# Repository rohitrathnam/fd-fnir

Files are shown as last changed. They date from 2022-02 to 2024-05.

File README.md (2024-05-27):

# Prototype Instrumentation for Frequency Domain fNIRS

## Abstract

Frequency domain fNIRS is a tissue optical measurement technique used to measure
absolute haemoglobin concentrations in brain tissue. This work is intended to
be the first step in the development of a wearable, low-cost FD-fNIRS device for
neurofeedback applications. The system requirements were generated from a review
of relevant literature. A simplified system architecture was developed based on the
various instrumentation methodologies proposed by various authors. The functional
blocks of this system were prototyped and their performance was evaluated. The
developed VCSEL current source was found to have a span of 10uA which meets the
design specifications. However, challenges exist in optimally biasing SiPM, which is
susceptible to optical and electronic noise sources.

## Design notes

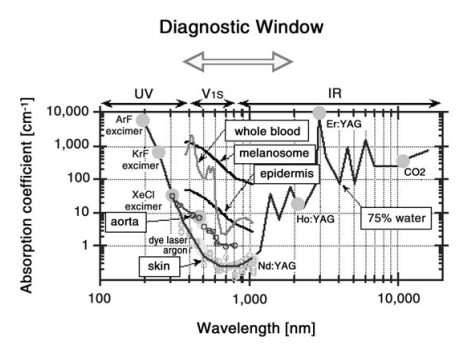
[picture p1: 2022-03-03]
optical_window.png

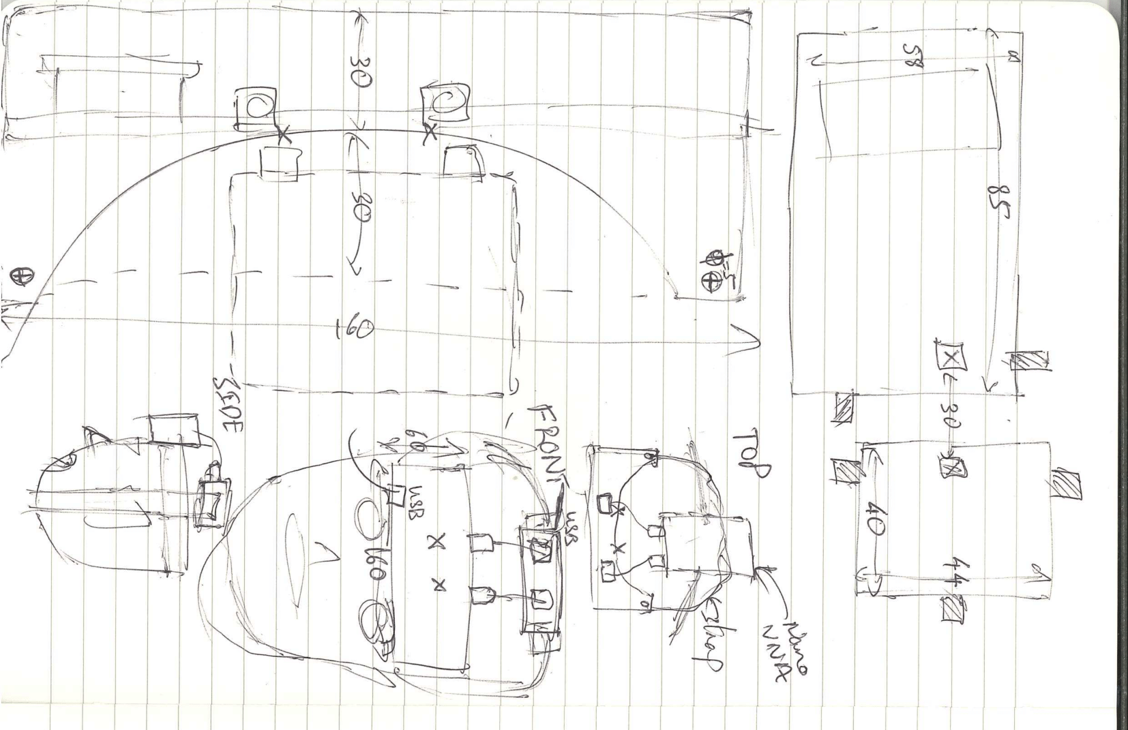
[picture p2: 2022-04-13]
drawings-hand-1.png

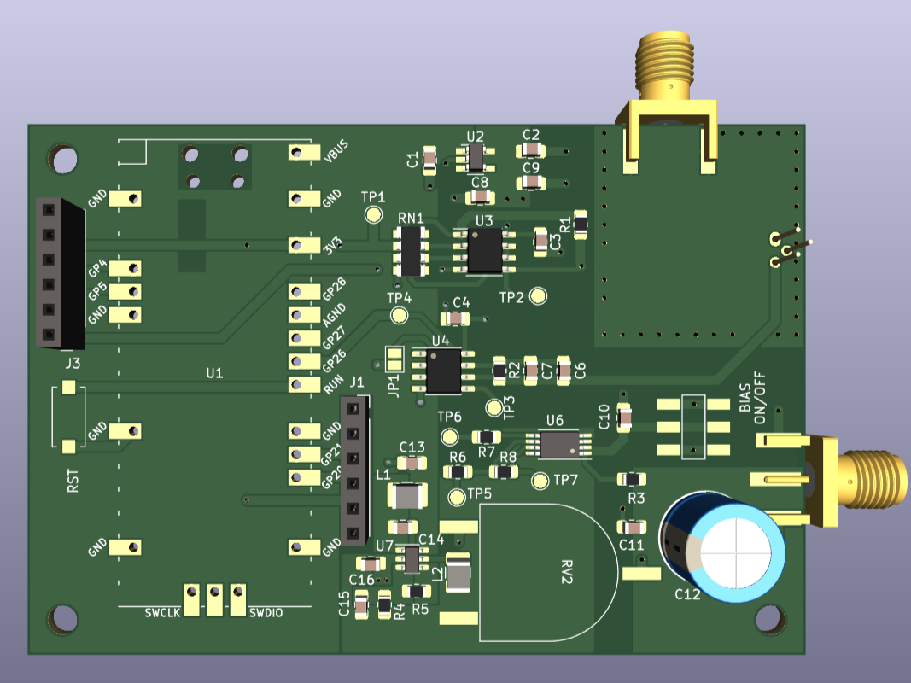
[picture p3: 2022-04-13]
driver-board/driver-board-front.png

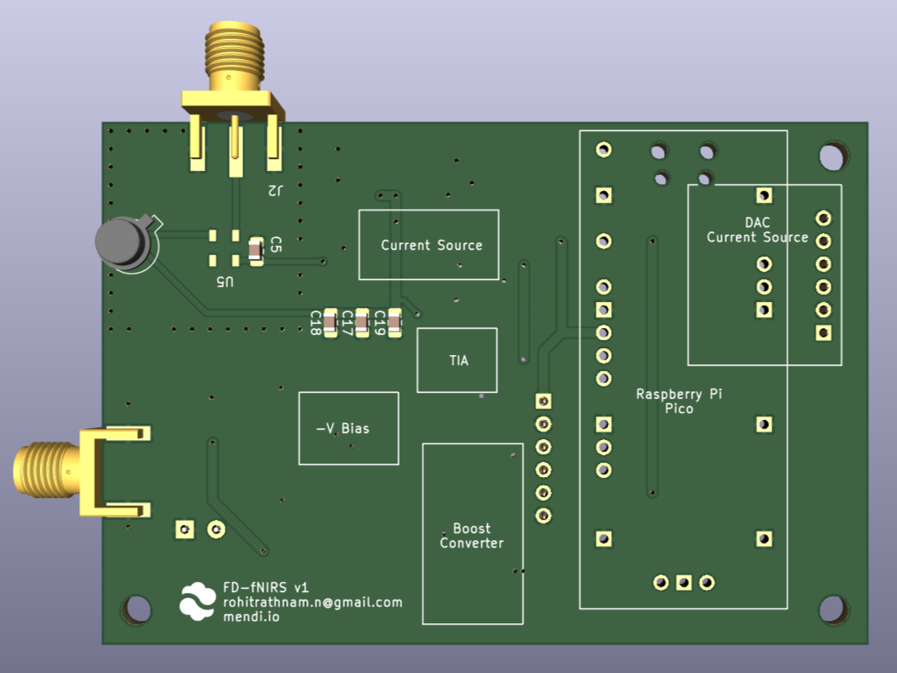
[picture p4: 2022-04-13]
driver-board/driver-board-back.png

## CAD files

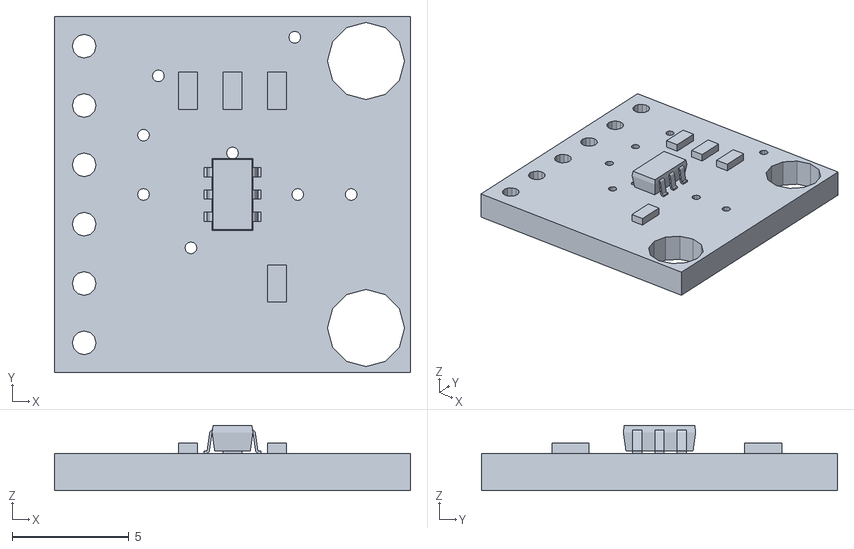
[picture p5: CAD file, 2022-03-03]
driver-board/MCP4725_Breakout.stl
15.2 x 15.2 x 2.80

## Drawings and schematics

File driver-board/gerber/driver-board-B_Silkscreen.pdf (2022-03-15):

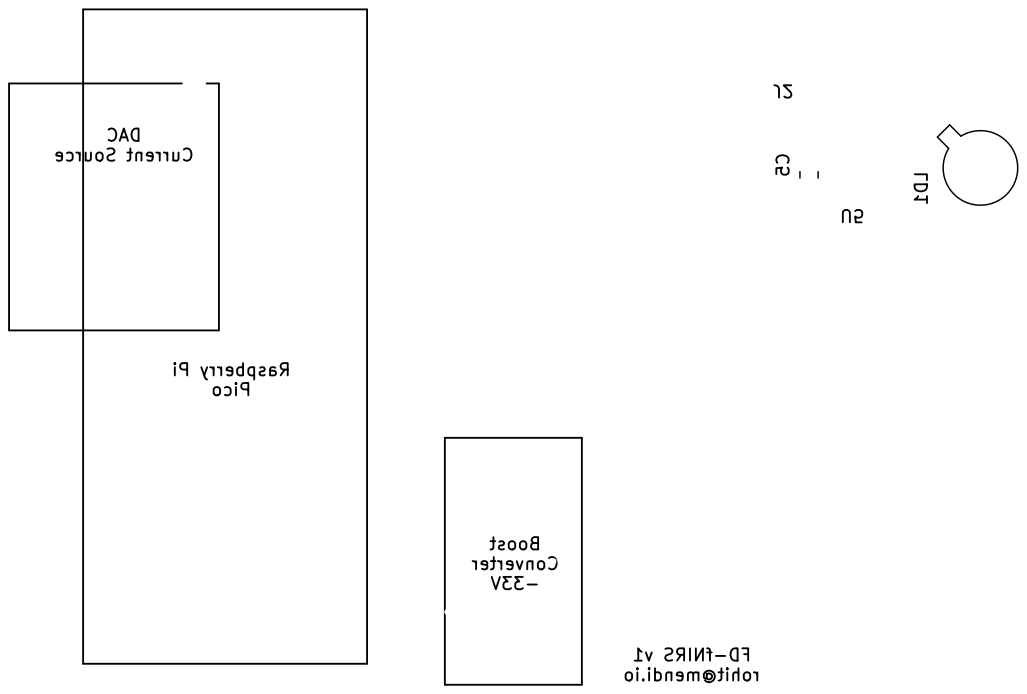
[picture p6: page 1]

Current Source FD-fNIRS v1

rohit@mendi.io Boost Converter

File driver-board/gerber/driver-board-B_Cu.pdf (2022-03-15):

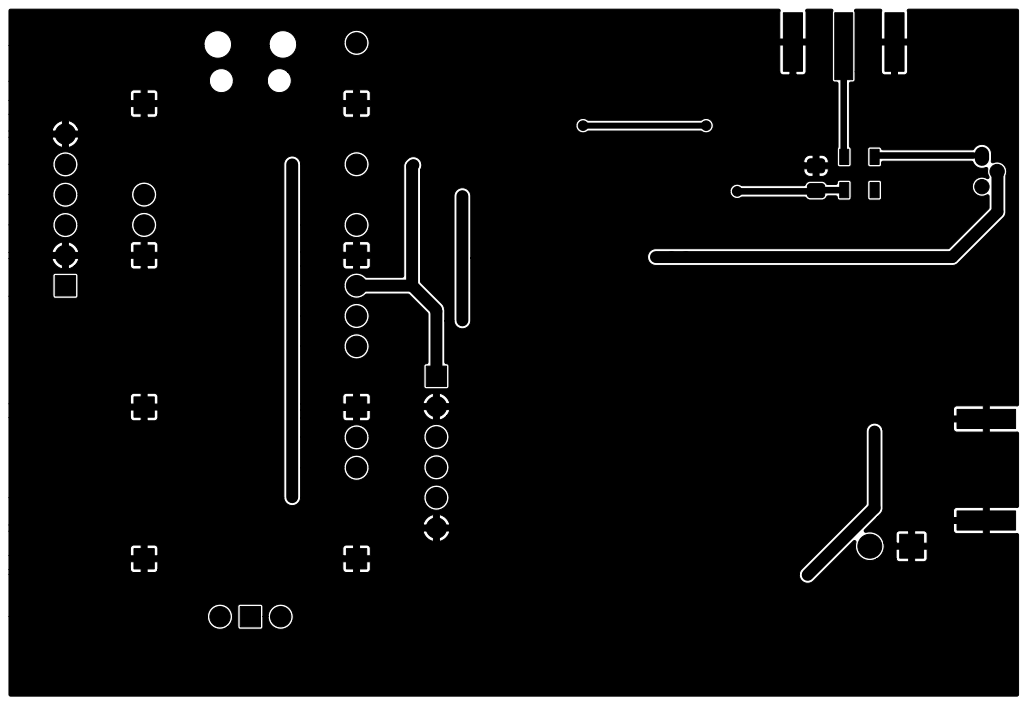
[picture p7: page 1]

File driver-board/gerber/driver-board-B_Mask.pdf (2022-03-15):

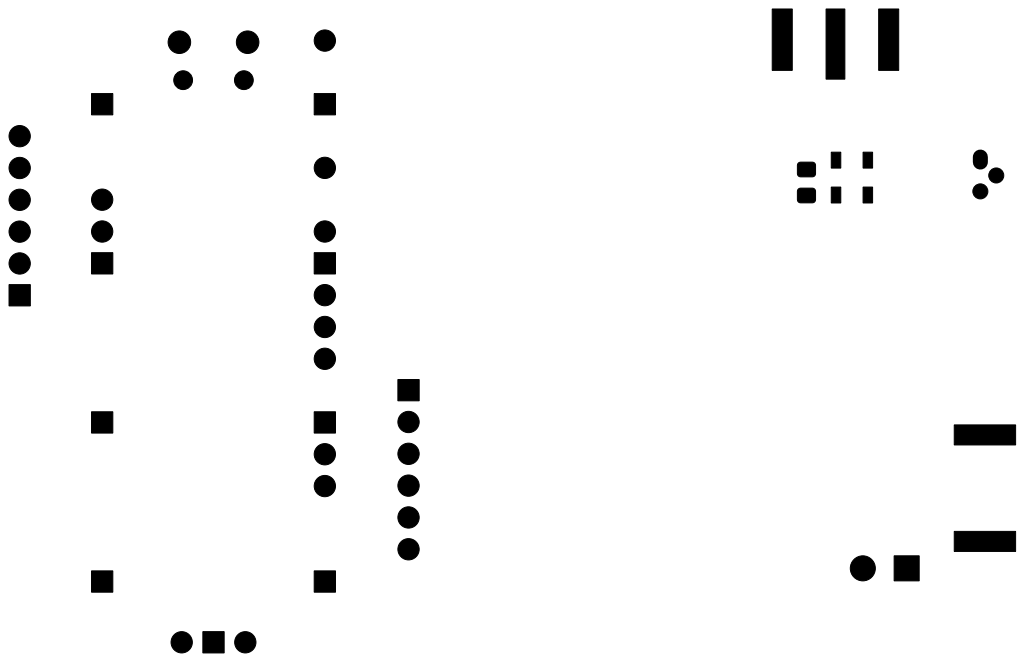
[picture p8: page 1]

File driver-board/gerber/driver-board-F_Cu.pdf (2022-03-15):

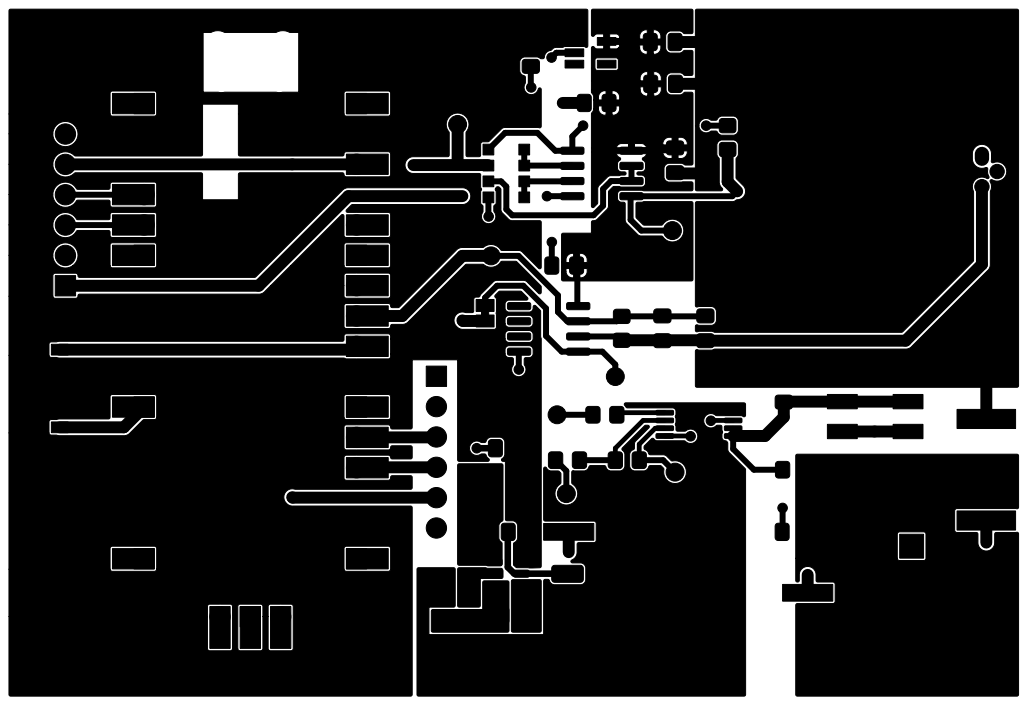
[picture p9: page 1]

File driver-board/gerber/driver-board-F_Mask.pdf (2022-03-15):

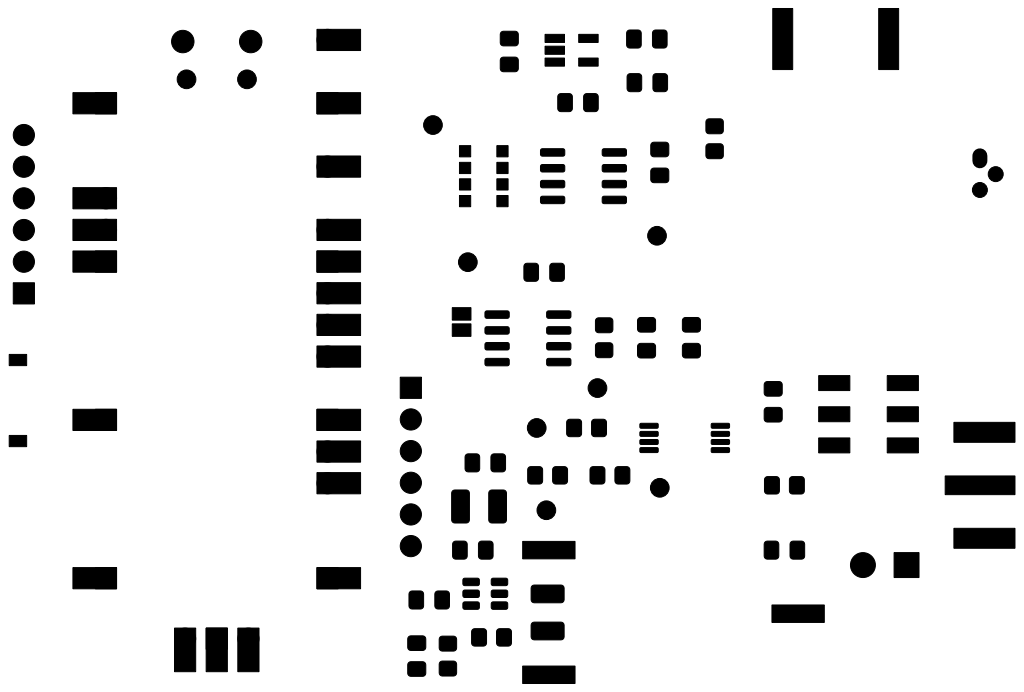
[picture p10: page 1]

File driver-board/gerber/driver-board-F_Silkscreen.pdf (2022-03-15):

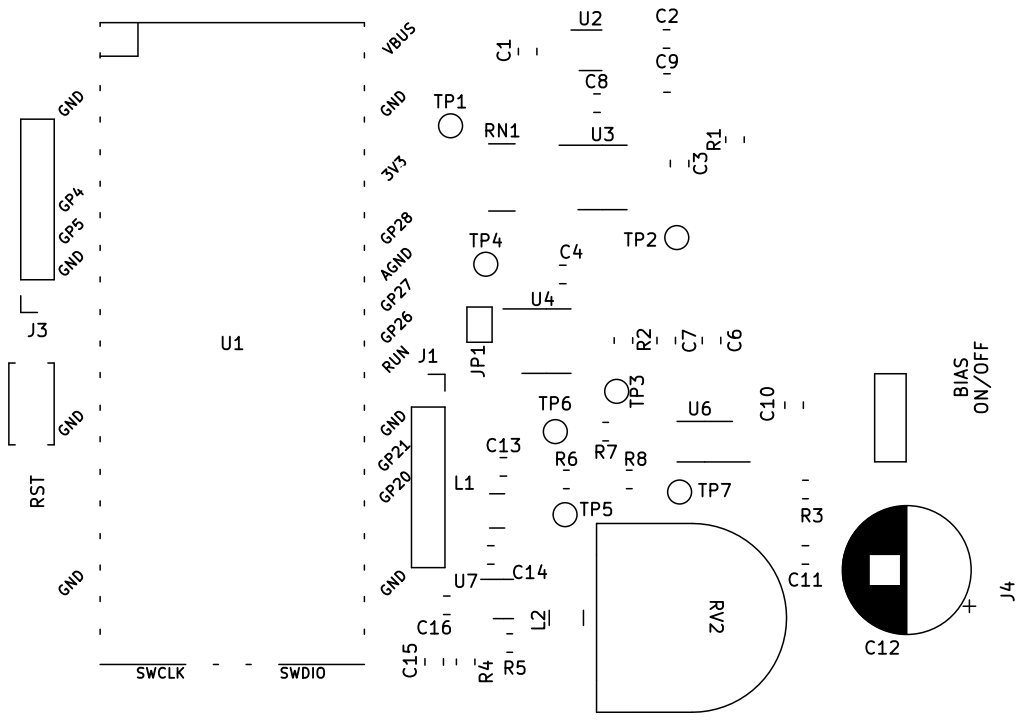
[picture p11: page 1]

RST BIAS ON/OFFU1 RUN GND GND GND GP21 AGND

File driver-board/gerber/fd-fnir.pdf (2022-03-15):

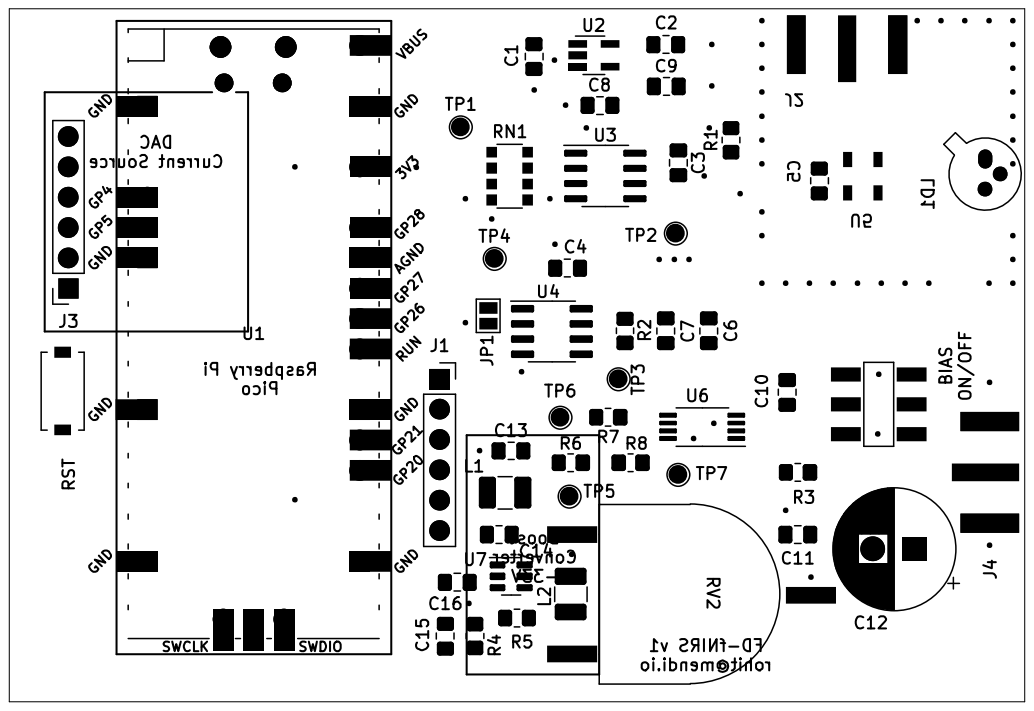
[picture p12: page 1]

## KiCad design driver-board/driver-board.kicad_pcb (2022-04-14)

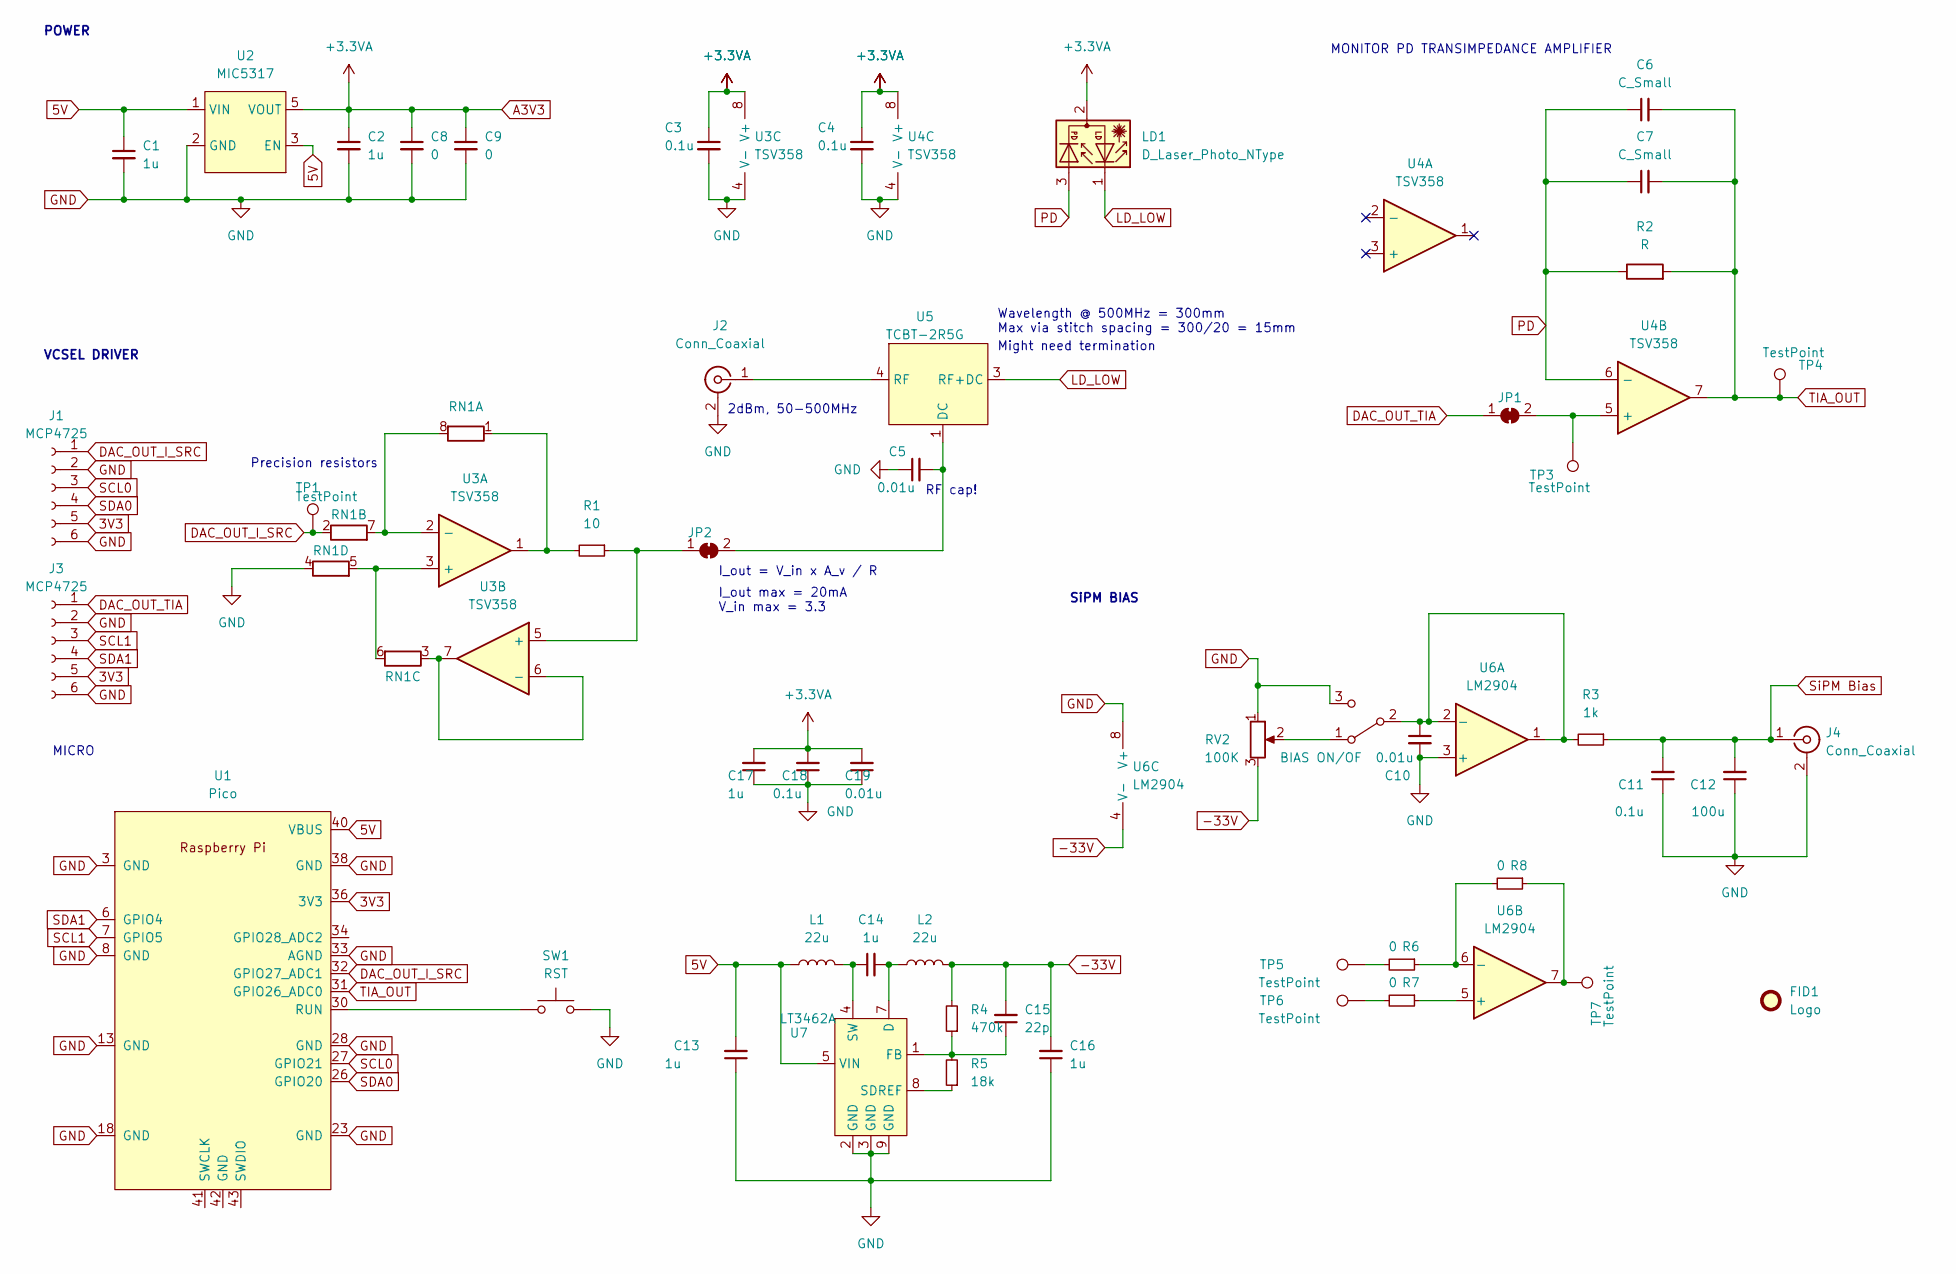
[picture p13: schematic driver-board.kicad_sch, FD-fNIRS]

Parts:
C1, C2, C13, C14, C16, C17: 1u; C_0805_2012Metric_Pad1.18x1.45mm_HandSolder
C3, C4, C11, C18: 0.1u; C_0805_2012Metric_Pad1.18x1.45mm_HandSolder
C5, C10, C19: 0.01u; C_0805_2012Metric_Pad1.18x1.45mm_HandSolder
C6, C7: C_Small; C_0805_2012Metric_Pad1.18x1.45mm_HandSolder
C8, C9: 0; C_0805_2012Metric_Pad1.18x1.45mm_HandSolder
C12: 100u; CP_Radial_D10.0mm_P3.50mm
C15: 22p; C_0805_2012Metric_Pad1.18x1.45mm_HandSolder
FID1: Logo; mendi-logo-plain
J1, J3: MCP4725; PinSocket_1x06_P2.54mm_Vertical
J2, J4: Conn_Coaxial; CONSMA020.062-G
JP1: SolderJumper_2_Open; SolderJumper-2_P1.3mm_Bridged_Pad1.0x1.5mm
JP2: SolderJumper_2_Bridged; SolderJumper-2_P1.3mm_Bridged_Pad1.0x1.5mm
L1, L2: 22u; L_1210_3225Metric_Pad1.42x2.65mm_HandSolder
LD1: D_Laser_Photo_NType; TO-46-3
R1: 10; R_0805_2012Metric_Pad1.20x1.40mm_HandSolder
R2: R; R_0805_2012Metric_Pad1.20x1.40mm_HandSolder
R3: 1k; R_0805_2012Metric_Pad1.20x1.40mm_HandSolder
R4: 470k; R_0805_2012Metric_Pad1.20x1.40mm_HandSolder
R5: 18k; R_0805_2012Metric_Pad1.20x1.40mm_HandSolder
R6, R7, R8: 0; R_0805_2012Metric_Pad1.20x1.40mm_HandSolder
RN1: R_Pack04_SIP_Split; ACASA5002S5002P1AT
RV2: 100K; PT15-RV15
SW1: RST; PTS636 SM43J
SW2: BIAS ON/OF; JS202011SCQN
TP1, TP3, TP4, TP5, TP6, TP7: TestPoint; TestPoint_Pad_D1.5mm
U1: Pico; RPi_Pico_minimal
U2: MIC5317; SOT-23-5_HandSoldering
U3, U4: TSV358; SOIC-8-1EP_3.9x4.9mm_P1.27mm_EP2.29x3mm
U5: TCBT-2R5G; TCBT
U6: LM2904; TSSOP-8_4.4x3mm_P0.65mm
U7: LT3462A

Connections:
3V3: J1.5, J3.5, U1.36 (3V3)
5V: C1.1, C13.2, L1.1, U1.40 (VBUS), U2.1 (VIN), U2.3 (EN), U7.5 (VIN)
-33V: C15.2, C16.2, L2.2, R4.2, RV2.3, U6.4 (V-)
A3V3: C2.1, C3.1, C4.1, C8.1, C9.1, C17.2, C18.2, C19.2, LD1.2, U2.5 (VOUT), U3.8 (V+), U4.8 (V+)
DAC_OUT_I_SRC: J1.1, RN1.2 (R2.1), TP1.1, U1.32 (GPIO27_ADC1)
DAC_OUT_TIA: J3.1, JP1.1 (A)
GND: C1.2, C2.2, C3.2, C4.2, C5.1, C8.2, C9.2, C10.2, C11.1, C12.1, C13.1, C16.1, C17.1, C18.1, C19.1, J1.2, J1.6, J2.2 (Ext), J3.2, J3.6, J4.2 (Ext), RN1.4 (R4.1), RV2.1, SW1.2, SW2.3 (C), U1.3 (GND), U1.8 (GND), U1.13 (GND), U1.18 (GND), U1.23 (GND), U1.28 (GND), U1.33 (AGND), U1.38 (GND), U2.2 (GND), U3.4 (V-), U4.4 (V-), U6.3 (+), U6.8 (V+), U7.2 (GND), U7.3 (GND), U7.9 (GND)
LD_LOW: LD1.1, U5.3 (RF+DC)
unnamed: C5.2, JP2.2 (B), U5.1 (DC)
unnamed: C10.1, R3.2, SW2.2 (B), U6.1, U6.2 (-)
unnamed: C14.1, L1.2, U7.4 (SW)
unnamed: C14.2, L2.1, U7.7 (D)
unnamed: C15.1, R4.1, R5.2, U7.1 (FB)
unnamed: J2.1 (In), U5.4 (RF)
unnamed: JP1.2 (B), TP3.1, U4.5 (+)
unnamed: JP2.1 (A), R1.1, U3.5 (+)
unnamed: R1.2, RN1.1 (R1.1), U3.1
unnamed: R5.1, U7.8 (SDREF)
unnamed: R6.1, R8.2, U6.6 (-)
unnamed: R6.2, TP5.1
unnamed: R7.1, U6.5 (+)
unnamed: R7.2, TP6.1
unnamed: R8.1, TP7.1, U6.7
unnamed: RN1.3 (R3.1), U3.6 (-), U3.7
unnamed: RN1.5 (R4.2), RN1.6 (R3.2), U3.3 (+)
unnamed: RN1.7 (R2.2), RN1.8 (R1.2), U3.2 (-)
unnamed: RV2.2, SW2.1 (A)
unnamed: SW1.1, U1.30 (RUN)
PD: C6.1, C7.1, LD1.3, R2.1, U4.6 (-)
SCL0: J1.3, U1.27 (GPIO21)
SCL1: J3.3, U1.7 (GPIO5)
SDA0: J1.4, U1.26 (GPIO20)
SDA1: J3.4, U1.6 (GPIO4)
SiPM Bias: C11.2, C12.2, J4.1 (In), R3.1
TIA_OUT: C6.2, C7.2, R2.2, TP4.1, U1.31 (GPIO26_ADC0), U4.7

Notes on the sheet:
Wavelength @ 500MHz = 300mm Max via stitch spacing = 300/20 = 15mm
2dBm, 50-500MHz
I_out = V_in x A_v / R
MICRO
MONITOR PD TRANSIMPEDANCE AMPLIFIER
Might need termination
VCSEL DRIVER
RF cap!
POWER
SiPM BIAS
I_out max = 20mA V_in max = 3.3
Precision resistors

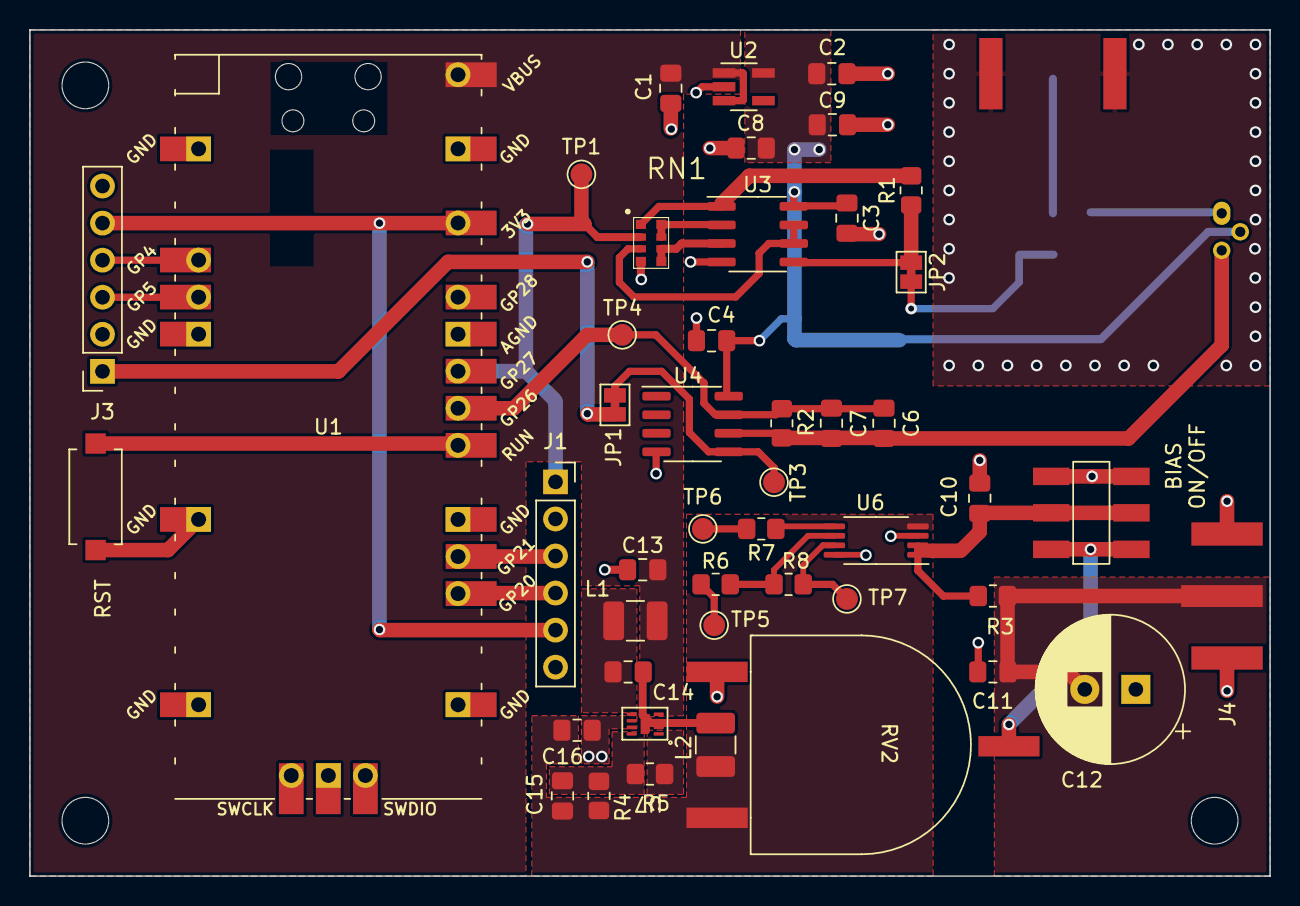
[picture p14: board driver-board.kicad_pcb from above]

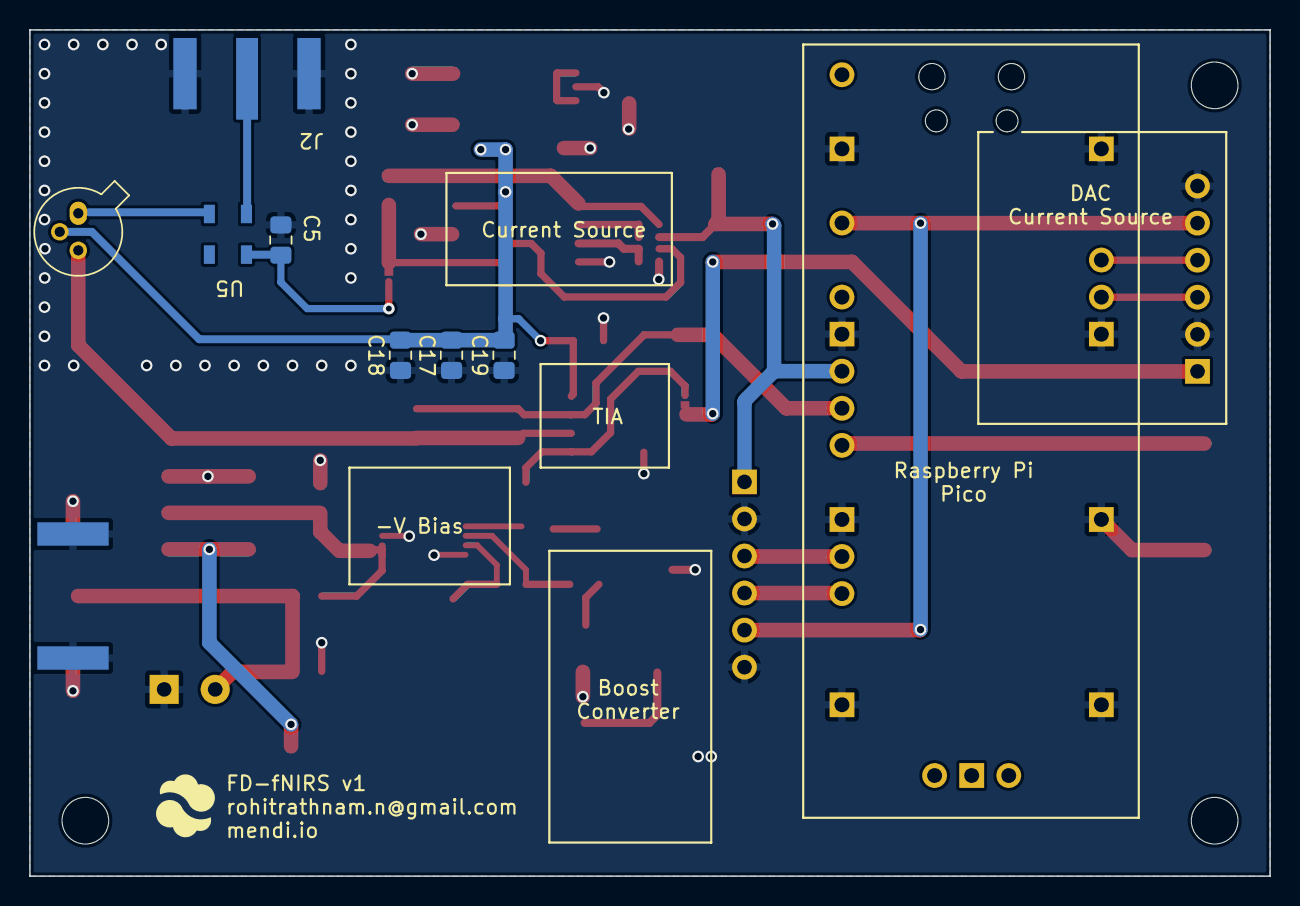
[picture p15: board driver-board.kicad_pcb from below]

Board: 2 copper layers, 85.0 x 58.0 mm, 54 parts (8 on the bottom side), 35 nets.

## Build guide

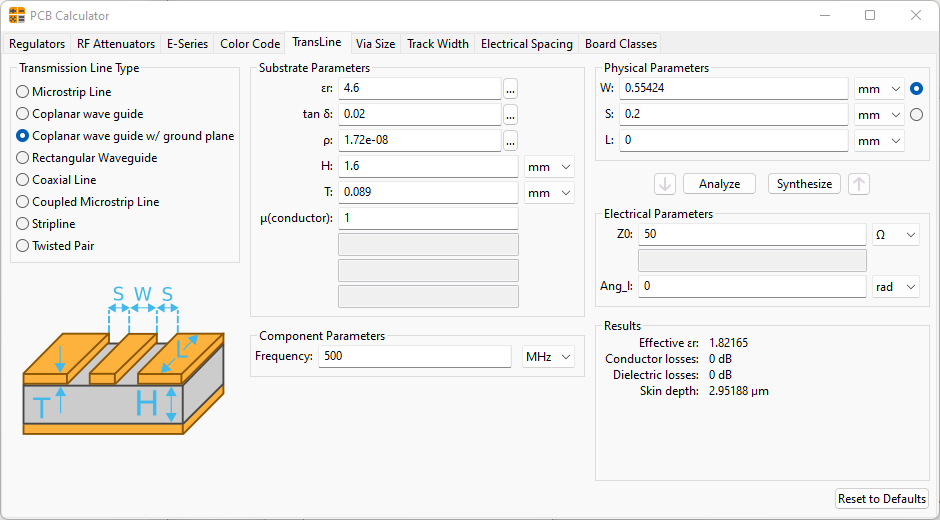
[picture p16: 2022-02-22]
coplanar-waveguide-gnd-plane.png

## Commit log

2022-02-22 sim files
    added sim files, separate kicad project for driver and receiver, trans line calc for PCB
    [driver-board.kicad_pcb, driver-board.kicad_sch, reciever-board.kicad_pcb, reciever-board.kicad_sch]
2022-02-24 Updated to low side driver
    modified schematic to low side driver, sim files for that, added footprints and 3D bodies for all components
    [CONSMA020.062-G--3DModel-STEP-56544.STEP, driver-board.kicad_pcb]
2022-02-24 fix pot footprint
    [driver-board.kicad_pcb, driver-board.kicad_sch]
2022-02-25 more test points and design rules
    [driver-board.kicad_pcb, driver-board.kicad_sch]
2022-03-08 pico modified sym/fp
    [driver-board.kicad_pcb]
2022-03-11 Passing DRC
    [driver-board.kicad_pcb, driver-board.kicad_sch]
2022-03-15 DRC passing, updated HV section and mounting
    [driver-board-B_Cu.gbr, driver-board-B_Mask.gbr, driver-board-B_Silkscreen.gbr, driver-board-Edge_Cuts.gbr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]
2022-03-16 Board reviewed, silk screen fixes
    [driver-board-B_Cu.gbr, driver-board-B_Mask.gbr, driver-board-B_Silkscreen.gbr, driver-board-Edge_Cuts.gbr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]
2022-03-16 changed design rules and via sizes for aisler
    [driver-board-B_Cu.gbr, driver-board-B_Mask.gbr, driver-board-B_Silkscreen.gbr, driver-board-Edge_Cuts.gbr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]
2022-04-13 added bom and pico code
    [driver-board.kicad_sch]
2022-04-14 fixed RN1 fp
    [driver-board.kicad_pcb, driver-board.kicad_sch]
2022-04-14 fixed U2-EN pin
    [driver-board.kicad_pcb, driver-board.kicad_sch]
2022-04-14 fixed lt3462 fp, routing pending
    [driver-board.kicad_pcb, driver-board.kicad_sch]
2022-04-14 updated rst button fp
    [driver-board.kicad_pcb]
